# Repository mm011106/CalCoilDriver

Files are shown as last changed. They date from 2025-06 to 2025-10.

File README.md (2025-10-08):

<!-- 
基本資料はこちら：
BOXで、 ESM50902 を検索
SQUID用と比べて電流値が大きかも。
 -->

> [!NOTE]
> 資料などについてコメント等あればDiscussionsに投稿ください。

# 機器名
### **キャリブレーションコイルドライバ　ER-524D**

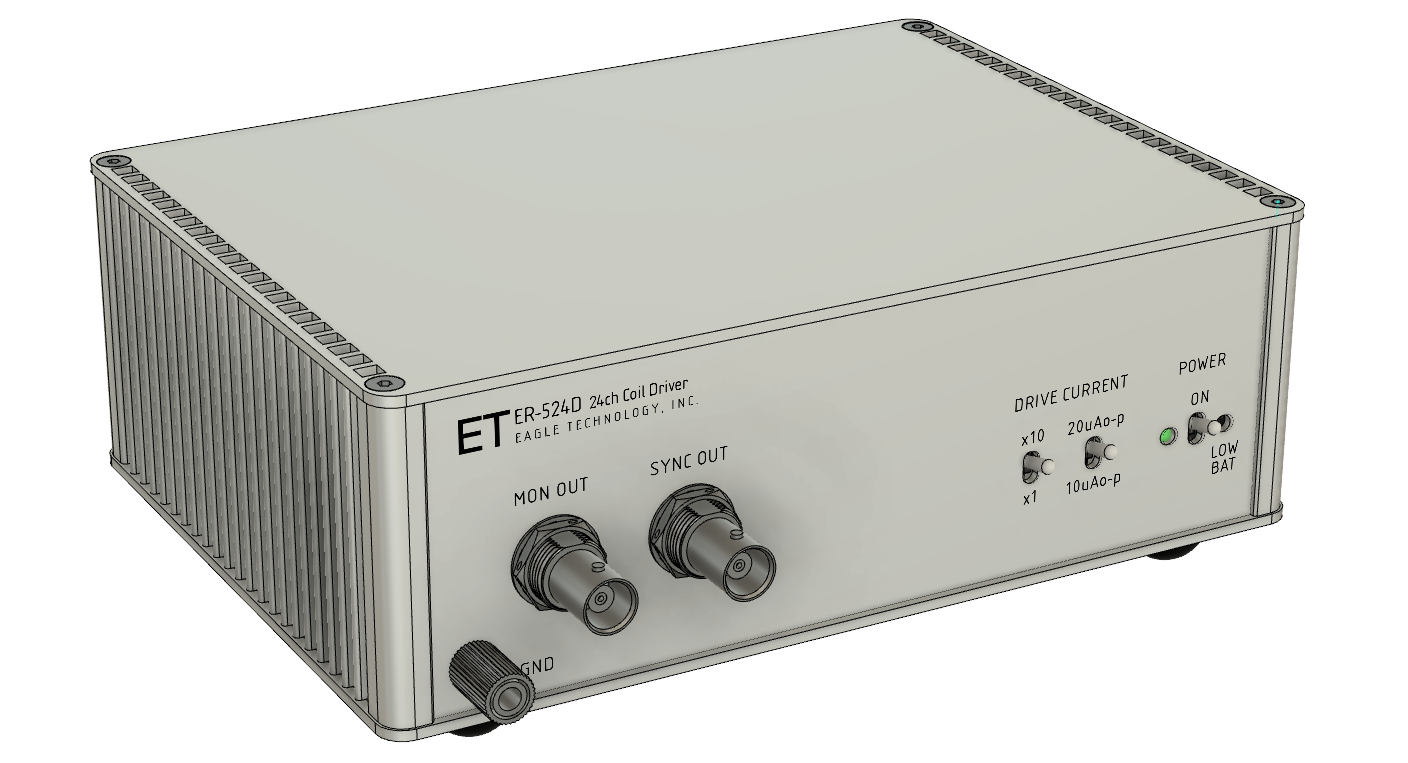
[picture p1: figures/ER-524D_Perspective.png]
3DPerspective


# 機器の概要

## 用途・目的
<!-- 本製品は磁気センサの感度・位置校正を行うための基準磁場を発生するためのコイルを定電流駆動する駆動回路です。
適切に設計・配置されたコイルでキャリブレーションコイルドライバにより基準となる磁場を発生させ、磁気センサから得られた磁場の強度信号とコイルドライバからの印加電流強度信号を以て磁気センサの感度・位置を校正することが可能です。 -->

複数の磁気センサをアレイ状に配置し磁場計測を行う場合、各センサ位置とその感度の両方を校正する必要があります。寸法や巻き数などのパラメタが管理されて製作されたコイル（キャリブレーションコイル）とそれを規定の電流で駆動する回路により基準となる磁場を発生させ、その磁場を計測することで校正が可能となります。この「キャリブレーションコイルドライバ」は校正作業に必要なキャリブレーションコイルを規定の電流で駆動するために設計された回路です。
> [!NOTE]
> 磁気センサの校正は以下の手順で行われます：
> 1. **センサとコイルの配置設定**：キャリブレーションコイル（複数）を校正対象の磁気センサに対して適切な位置に配置
> 2. **基準磁場の発生**：コイルドライバにより既知の強度の磁場を複数の異なる場所で発生させ、その磁場を校正対象のセンサで計測する
> 3. **信号計測**：発生した磁場の強度を磁気センサで測定すると同時に、コイルドライバのモニタ端子からコイルに流れた電流を計測
> 4. **校正実行**：両者の計測結果を基に磁気センサの感度と位置を校正

## 機能
- 交流の電流を各コイルに時分割で供給し駆動します。
- 各コイルの駆動はバースト波状の正弦波信号です。
- コイルを駆動する電流はパネルのスイッチで切り替えが可能です。
- コイルに流れる電流は電圧としてモニタができます。
- 流れている電流と上記のモニタ端子の電圧を測定器を用いて値づけすることにより、コイルに流れる電流値が計測できます。
- 単三型充電池4本で動作します。

## 性能
- 駆動信号周波数： 80Hz
- 駆動電流波形：正弦波
- 電流出力：200 / 100 / 20 / 10 [μAo-p]
- 駆動チャネル数：24（設計により変更可能）
 
> [!NOTE]
>  **駆動対象**
> 駆動の対象となるコイルは、十分直流インピーダンスが低く、インダクタンスが小さいことを想定しています。駆動回路の出力インピーダンスは10kΩ程度となっているため、コイルの直流インピーダンスが大きいと規定の電流を流せなくなる可能性があります（動作に支障はありません）。インダクタンスについては1mH以下を想定しています。駆動周波数80Hzでのコイルのインピーダンスが十分小さいことを条件として設計しています。
 <!-- 出力インピーダンス10kΩとして、1mH負荷のときのHPF遮断周波数は1.6MHz 一方、1mHの80Hzでのインピーダンス（リアクタンス）は0.5Ω -->

> [!NOTE]
>  **駆動回路**
> 駆動回路は高インピーダンス出力の非安定化電流源となっています。負荷接続時に定電流制御する回路は実装されていません。
> 負荷となるコイルがよく管理されて製造されているためコイルのインピーダンスのばらつきが非常に小さく、インピーダンスそのものも小さいと想定できたため、簡便な回路としました。

## バリエーション
本器の「負荷に電流を供給しその電流値を計測する」という機能により、生体磁場信号をエミュレートするための「ファントムコイル」をドライブすることに最適化した「ファントムドライバ」を作成可能です。磁場センサのキャリブレーションとは異なる電流設定（磁場強度設定）が必要な場合は出力電流の再設計が必要です。
> [!NOTE]
> **駆動電流の変更**
> 駆動電流の変更には回路定数の変更が必要となります。使用しているデバイスの性能から駆動電流の最大値は5mAo-p程度です。これ以上の電流が必要な場合は、回路定数の変更と同時にオペアンプの変更を検討してください。
>
> 

# 機器の構成 
コイルを駆動するための回路本体のみです。
キャリブレーションコイルそのものについては、この設計情報に含まれません。

# 動作の概要

### 駆動可能なコイルの数
この回路で駆動できるコイルの数は24個です。キャリブレーションコイルは３軸方向に磁場を発生させることを想定しており、３個のコイルが１つのコイルセットとなり、さらにそれを８個（３軸のコイルセットを８個）駆動できます。
駆動のための信号は多ピンコネクタ（ハーフピッチ50pin-SCSIコネクタ）に出力されますので、適宜コイルと接続するためのジグやケーブルの製作が必要となります。
> [!NOTE]
> 多ピンのコネクタは近年入手が困難になってきています。新たに製作される場合は3ピン〜6ピン程度の小型コネクタを複数利用するのが得策かと思います。

回路設計としては最大50個のコイルが駆動できるようになっていますので、ユーザの用途に応じてチャネル数を変更できます。

### 駆動波形
駆動は内部の正弦波発振回路に同期した正弦波のバースト波により時分割で行われます。駆動の様子を図示しました。
24個のコイルの駆動が1つのコイル駆動シーケンスとなり、それが繰り返されます。

まず、そのシーケンスの開始を示すため同期信号が正弦波の1周期の時間だけアサートされます。
同期信号がネゲートされると最初のコイルが駆動が始まります。
コイルは正弦波の24周期の時間だけ駆動され、1周期分の駆動休止時間が続き、次のコイルの駆動へと移ります。
最後のコイルが駆動された後、正弦波25周期分の長い駆動休止時間があり、コイルドライブの1周期が完了します。

駆動するコイルの順番やチャネル数、バースト波の波数と休止波数、正弦波の周波数は回路（HDL）で設定することができます。デフォルトでは、チャネル数24、正弦波の周波数80Hz、バースト波の波数24、休止波数1となっています。

<!-- 駆動用の正弦波は内部(DDSによる)で生成していますが、外部から供給することも可能です。この場合、信号の振幅が直接コイル駆動の電流値に変換されますので、供給する信号の振幅設定を確認してご利用ください。 -->

（下記「コイル駆動のタイミングチャート」を参照）

### 電流モニタ端子
コイルに流れる電流をモニタするための端子を備えています。
アナログ電圧出力で、0A = 1.65V となっています。
電流・電圧変換係数は、設計値で5033[V/I]となっています。

### 駆動電流の切り替え
駆動電流は、10μAo-p, 20μAo-p, 100μAo-p, 200μAo-pの４点切り替えです。
2つのトグルスイッチで設定します。

### 同期信号
24個のコイル駆動シーケンスの最初に正弦波の1周期の時間だけアサートされます。
レベルは0−3.3V、アクティブHi（正論理）です。

# 仕様
- ドライブコイル数：24
<br></br>
- 駆動電流 　(スイッチによる　4点切り替え)
  - 10/20/100/200μAo-p
<br></br>
- インターフェイス </br>
  - 同期信号出力：0−3.3Vロジック出力（正論理）
  - 駆動電流モニタ出力
    - アナログ電圧による（1.65V中心に+/-1V振幅）
    - 電流電圧変換係数：5033\[V/I] (設計値)
<br></br>
- 操作：フロントパネルトグルスイッチによる電源のOn/Off
<br></br>
- 表示
  - 電源電圧低下警告 Low-Battery（LED:赤）
  - 動作表示 (LED:緑)
<br></br>
- 電源：単三充電池（Ni-MH）4本
<br></br>

### コイル駆動のタイミングチャート
<!-- ![drive timing chart](figures/deriveSequence.png) -->
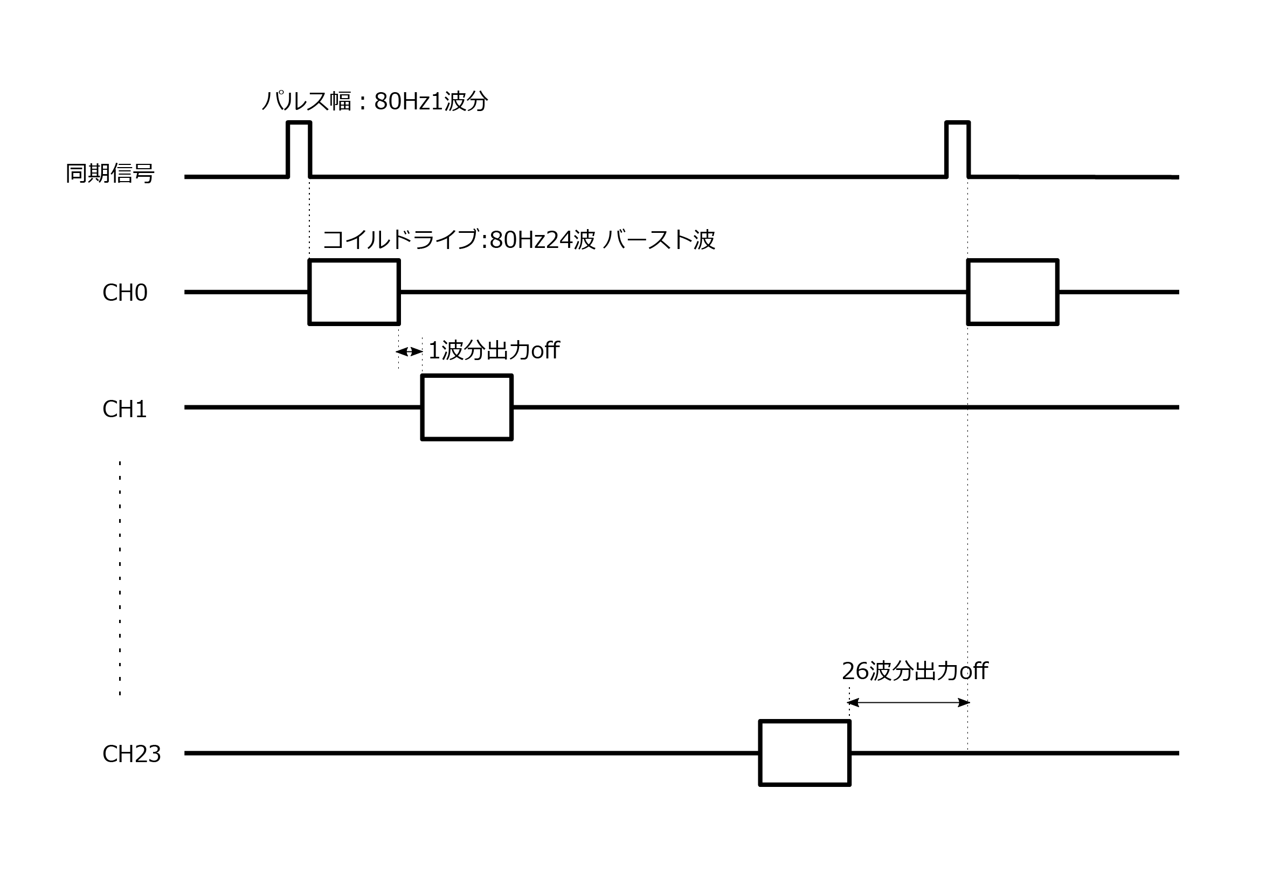
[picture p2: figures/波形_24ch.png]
drive_timing


### ブロック図
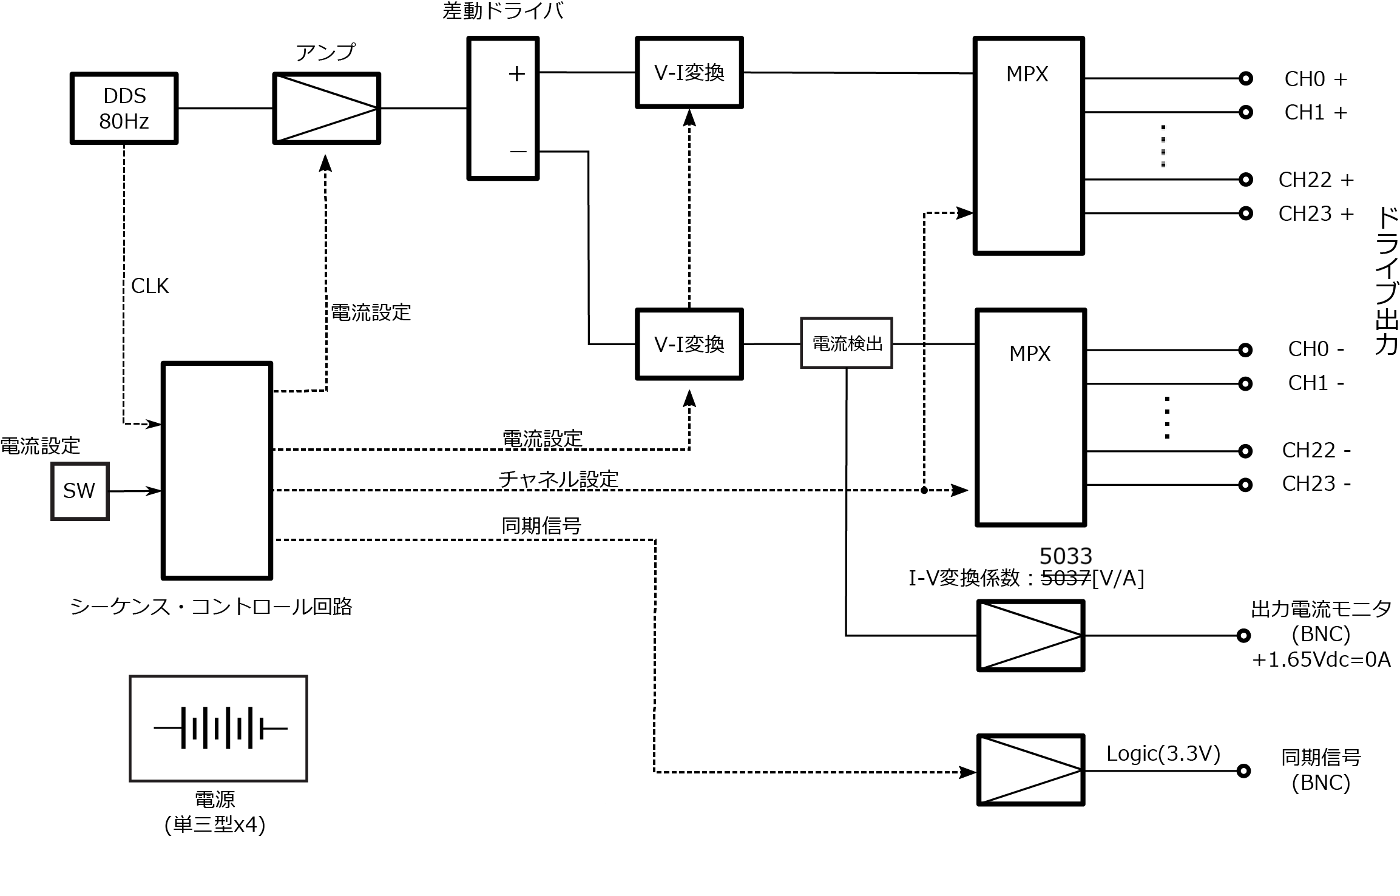
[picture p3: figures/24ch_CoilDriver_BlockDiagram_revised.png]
ER-524_BlockDiagram


</br>

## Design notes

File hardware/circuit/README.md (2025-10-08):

# このディレクトリについて

- このディレクトリにはPDF版の回路図が入っています。</br>
    CADを起動することなく回路図を確認することができます。

- 設計内容の詳細については[design_note](/hardware/circuit/design_note.md)を参照してください</br>

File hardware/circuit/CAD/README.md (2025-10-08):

# このディレクトリについて
このディレクトリは回路図・基板CADのプロジェクトが保管されています。</br>

CADにはEAGLEを使っています。 Ki-CADでインポート可能かと思います。

## 構成
[本体](/hardware/circuit/CAD/ER524D_CoilDriver24_EagleCAD/ER-524D_CoilDriver24.sch)：本体の回路図です。

[ハーネス](/hardware/circuit/CAD/ER524D_CoilDriver24_EagleCAD/harness_set.sch):装置内の盤間配線用ハーネスの回路図です。

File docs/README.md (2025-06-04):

# このディレクトリについて
このディレクトリは仕様書や製造に必要な書類、手順書などを保存してあります。

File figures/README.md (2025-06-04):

# このディレクトリについて
このディレクトリはリポジトリ内のドキュメントに挿入する図や写真などを保管する場所です。

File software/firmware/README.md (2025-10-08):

# このディレクトリについて

- このディレクトリはマイコンのファームウエア開発用IDEのプロジェクトフォルダを保管してあります。</br>
  この機器にはマイコンを使用しておりませんので、ファームウエアはありません。

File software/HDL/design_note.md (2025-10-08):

# 設計ノート
このノートは当該機器に使用しているHDLの設計意図を記録しています。</br>
回路動作の理解や改善・修理などにご利用ください

## 修正履歴
- 初版：2025/9/24  宮本政和

## 機能
- DDSを指定の周波数に初期設定する
- 80Hz発振器(DDS)をクロックとして、指定された波数と休止時間のバースト波を作るためのロジックと、それを最大50chのコイルに分配するためのチャネル指定信号を作成
- 機器の調整・試験のためのテストモードの設定

HDLのエンティティ名が`PHANTOMDRIVER`となっており製品型式名と異なりますが、回路設計の元となったコードのエンティティ名をそのまま残しています。
  
### ブロック図
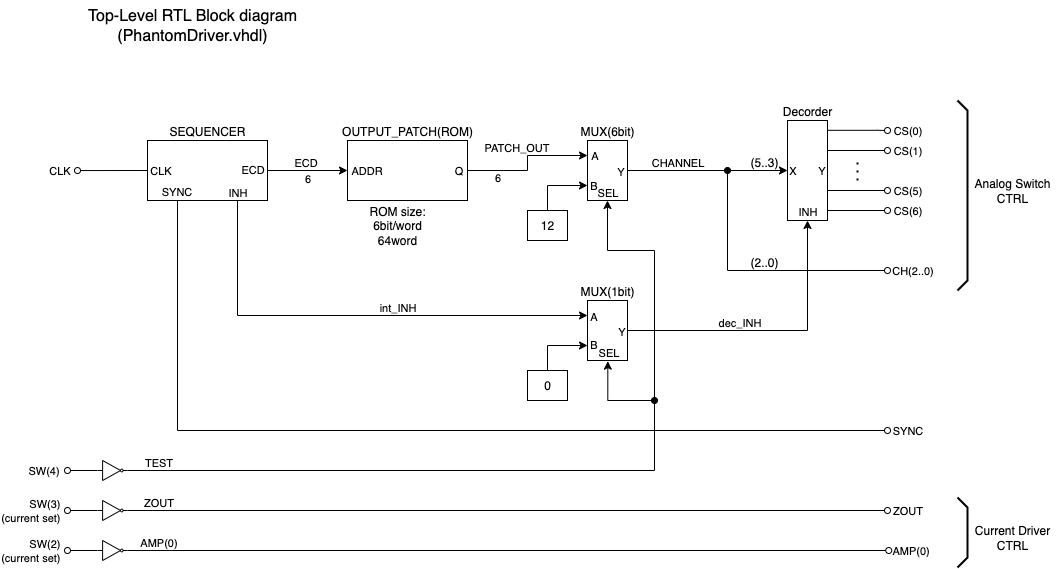
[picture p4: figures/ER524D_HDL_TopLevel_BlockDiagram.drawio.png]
Block Diagram for calibration

- DDSの初期設定回路については、このブロック図に記載していません

## 詳細動作
このHDLで記述されている機能は以下の通りです。
### 機能１ : DDSの初期化  ```DDS_INIT```
  DDSの出力が指定の周波数の正弦波になるよう初期化します。初期化にはSPIフォーマットのインターフェイスを用います。
  周波数はHDLのコンパイル時にハードコーディングされますので、周波数変更の場合はソースコードを変更しコンパイルが必要です。

### 機能2 : バースト波作成のための制御信号作成  ```SEQUENCER```
バースト波を作成するための制御信号をアナログ回路に提供し、連続した正弦波から指定された波数・休止のバースト波を作ります。
さらに規定の数のコイルを順次切り替えながらドライブするための制御信号を作成します。

### 機能3 : 駆動するコイルの切り替え  ```OUTPUT_PATCH``` ```MUX``` ```Decorder```
```SEQUENCER```からの信号を元にどのコイルをドライブするかを決定し、アナログ回路に提供します。

### 機能4 : ドライバ回路の設定  
フロントパネルにある電流設定スイッチの内容を読み、アナログ回路に提供します。

## 使用デバイス
- ALTERA MAX-V:  **5M160ZT100**
  - 温度グレード、スピードグレードは任意
- パッケージ：QFP-100pin

## ピンアサイン

| HDL信号名 | I/O |ピン番号 | 回路図信号名 |説明|
--|--|--|--|--
| CS[0] | O | 2 |#CS0|アナログスイッチCS信号
| CS[1] | O | 3 |#CS1|アナログスイッチCS信号
| CS[2] | O | 4 |#CS2|アナログスイッチCS信号
| CS[3] | O | 5 |#CS3|アナログスイッチCS信号
| CS[4] | O | 6 |#CS4|アナログスイッチCS信号
| CS[5] | O | 7 |#CS5|アナログスイッチCS信号
| CS[6] | O | 8 |#CS6|アナログスイッチCS信号
| LOW_BAT | I | 12 |#LOW_BAT|バッテリ低下検出
| CH[2] | O | 14 |CH_2|アナログスイッチチャネル設定信号
| CH[1] | O | 15 |CH_1|アナログスイッチチャネル設定信号
| CH[0] | O | 16 |CH_0|アナログスイッチチャネル設定信号
| OE    | O | 17 |#OE| （未使用）
| CLK   | I | 18 |SYNC_OSC| クロック入力（80Hz）
| AMP[0] | O | 19 |AMP_0| ドライブ回路電流設定（利得） 
| AMP[1] | O | 20 |AMP_1| ドライブ回路電流設定（利得）
| ZOUT   | O | 21 |ZOUT| ドライブ回路電流設定（インピーダンス）
| SEL_ANALOG | O | 26 | ANALOG / !DDS | 発振器指定出力
| SEL_EXT | O | 27 | EXT / #INT | 発振器外部・内部設定出力
| SW[5] | I | 51 |SW_DDS / #ANALOG|スイッチ入力 発振器指定
| SW[1] | I | 52 |SW_INT / #EXT|スイッチ入力 発振器外部・内部指定
| SW[2] | I | 53 |SW_x1 / #x2|スイッチ入力 ドライブ回路電流設定（利得） 
| SW[3] | I | 54 |SW_x1 / #x10|スイッチ入力 ドライブ回路電流設定（インピーダンス） 
| SW[4] | I | 55 |SW_#TEST|スイッチ入力 TEST動作設定 
| D[1] | O | 56 |DISP1|LED 発振器外部・内部表示
| D[2] | O | 57 |DISP2|（未使用）
| D[3] | O | 58 |DISP3|（未使用）
| D[4] | O | 61 |DISP4|（未使用）
| MCLK | I | 64 |MCLK| DDS:動作クロック
| SYNC | O | 66 |FRAME_SYNC|コイルドライブ同期信号
| PSEL | O | 70 |PSEL| DDS設定（未使用）
| FSEL | O | 71 |FSEL| DDS設定（未使用）
| RESET | O | 72 |RESET|DDS:リセット
| SDATA | O | 73 |SDATA|DDS:設定用SPI (DATA)
| SCLK | O | 74 |SCLK|DDS:設定用SPI (CLK)
| FSYNC | O | 75 |FSYNC|DDS:設定用SPI (STROBE)

---
## 回路構成
機能ブロックごとに詳細を記述します。

### ```DDS_INIT```
DDS-ICの初期化を行います。
- **INPUT:** </br>
    DDS_FREQ：DDSの周波数設定
    MCLK：DDSモジュールからのクロック(67.108864MHz)
- **OUTPUT:** </br>
    nRES, PSEL, FSEL, RESET：DDSのコントロール
    SDATA, SCLK, FSYNC：DDS設定端子(SPI)

#### 回路動作／設計のポイント
この回路は起動時に1回だけ動作する、DDSを初期化（周波数設定）する回路です。
設定はSDATA, SCLK, FSYNCの3つの端子(SPI)を操作することで行います。
この回路の動作クロックはDDSモジュールのクロック（67.108864MHz）から作成されています。
SPIのクロックは約1MHzに設定されています。

回路内に16bit長の設定データを3ワード分保持しており、これをMSBファーストでSDATA端子に出力していきます。
1ワードごとにFSYNC（負論理）の操作が必要で、この設計ではSPIクロックの1つ分の時間をFSYNCのアサート時間としています。

SPIにデータが出力される時のタイミングチャートを示します。参考にしてください。
<img src="/figures/HDL_DDS_INIT_SPI_timing.png" alt="Block Diagram for calibration" width="600px">

### ```SEQUENCER```
バースト波を作成するための制御信号をアナログ回路に提供し、連続した正弦波から指定された波数・休止のバースト波を作ります。
さらに規定の数のコイルを順次切り替えながらドライブするための制御信号を作成します。

- **INPUT:** </br>
  CLK: クロック入力（80Hz）
- **OUTPUT:** </br>
  SYNC: 同期信号
  指定数のコイルを順次ドライブしますが、その周期の最初に1回だけこの同期信号が１クロック時間だけアサートされます。
  INH: バースト波の「スペース」タイミングの指示
  この信号がアサートされている間、コイル駆動をoffにしてバースト波を作成します。
  ECD(6): コイルの番号
  この番号は'0'から'コイル数−1'の範囲となります。この数字は0からインクリメントされるので、この値を元に実際にどのコイルをドライブするのかを"OUTPUT_PATCH"で決定します。

この回路をインスタンス化する時のパラメータ指定例を示します。  
ここでは、コイル数24、バースト波 ON:24＋OFF:1
``` vhdl
-- コイル数の定義
  constant ECD_COUNT 	: integer :=24;   -- コイル数
  constant ECD_W		: integer :=integer(Ceil(log(real(ECD_COUNT-1),2.0)));   -- コイル数を数えるカウンタの幅

  constant BURST_MARK		: integer := 24;  -- バースト波の波数
  constant BURST_SPACE	: integer := 1;  -- バースト波の休止波数

-- インスタンス化
  SEQUENCER: entity work.SEQUENCER
    generic map (
      ECD_NUMBER => ECD_COUNT,
      ECD_Q_WIDTH => ECD_W, 
      BURST_MARK => BURST_MARK,
      BURST_SPACE => BURST_SPACE
    )
    
    port map (  -- 入出力信号の接続
      nRES => nRES, CLK => CLK,
      SYNC => SYNC, INH => int_INH, ECD => ECD
    );
```
  
#### 回路動作／設計のポイント
バースト波の波数をカウントするQ_BURSTカウンタと、コイルの番号をカウントするQ_ECDの2つのカウンタを設定しています。
これらの値から全コイルスキャンの同期信号SYNCと, アナログマルチプレクサを全てoffにして駆動のない状態を作るためのINH信号を作成しています。  
タイミングチャートを示します。参考にしてください。

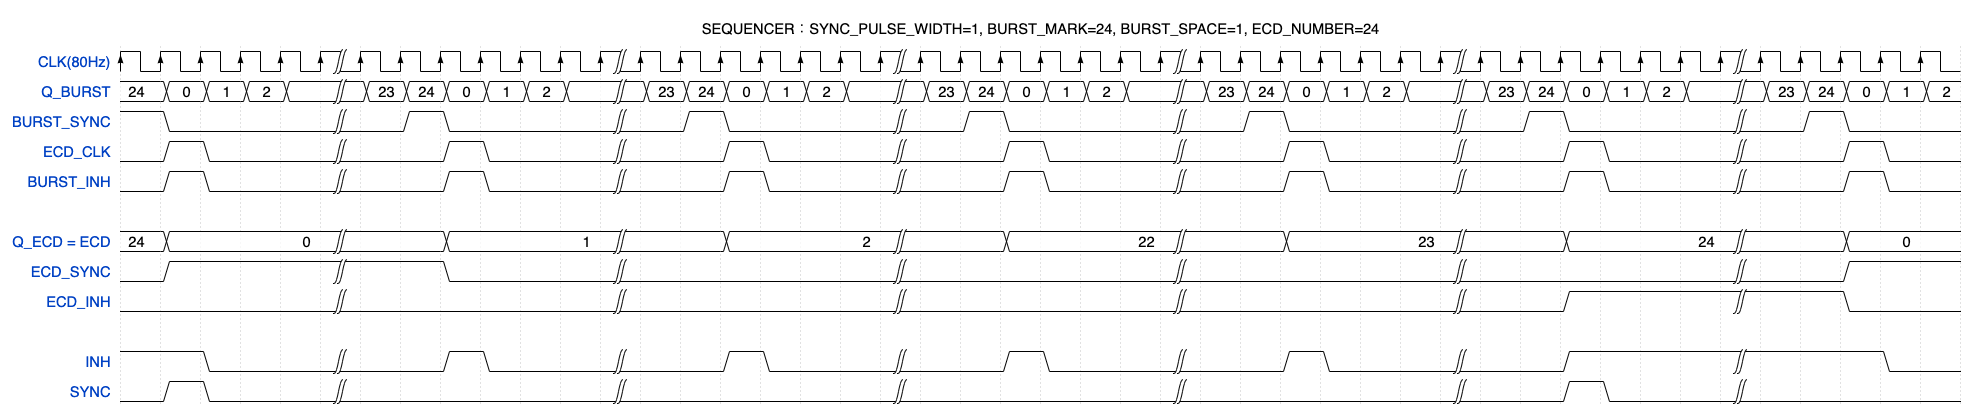
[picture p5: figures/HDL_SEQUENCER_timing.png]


### ```OUTPUT_PATCH```
```SEQUENCER```から出力されるECD番号をそれに対応するコイル番号に変更するためのROMです。

- **INPUT:** </br>
  ADDR: ECD番号の入力

- **OUTPUT:** </br>
  Q: ROMの値の出力
#### 回路動作／設計のポイント
これは単純なROMで、ADDRに入力された値からROMのデータを読み、その値をQに出力します。
この設計では、ADDRにSEQUENCERから出力されるECD番号が入力されその値に対応したコイル番号がQに出力されます。これにより、SEQUENCERでの番号（ECD番号）とコイル番号を対応づけています。
ADDR、Qともに6bit幅です。

ROMの値は ```patch_table.mif``` というファイルにテキスト形式で記述されています。

### TESTモード設定
コイルドライブの電流値キャリブレーション作業用にドライブするコイルを固定する回路です。
コイル番号を固定し、出力インヒビット信号を常にネゲートすることで、駆動するコイルを固定します。
（ブロック図中央、二つの```MUX```）

### ```Decorder```
- **INPUT:** </br>
  CHANNEL(5..0) : コイル番号
- **OUTPUT:** </br>
  CS(0)〜CS(6) : アナログマルチプレクサドライブ用チップセレクト信号
  CH(2..0) : アナログマルチプレクサドライブ用チャネル設定信号
  
#### 回路動作／設計のポイント
この回路の出力が直接アナログマルチプレクサIC14個（ドライブのプラス側、マイナス側それぞれに1個づつ使用）を制御します。
この信号によって制御されたアナログマルチプレクサにより、規定のバースト波が作られると共にコイルのスキャンが行われます。

## 注意事項
コイル数、バースト波などの設定をパラメタ化して任意の組み合わせで合成できるようにしていますが、全ての設定値の組み合わせでコンパイルが成功することを確認していません。パラメタを変更した場合は動作を確認してからご利用になるのがいいと思います。  

<!-- ## 変更履歴
##### 20xx/xx/xx Release1.0
- リリース内容メモ -->

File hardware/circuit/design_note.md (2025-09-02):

# 設計ノート
このノートは当該機器の電子回路設計の履歴や設計意図を記録しています。</br>
回路動作の理解や改善・修理などにご利用ください

## 修正履歴
- 初版：2025/06/01  宮本政和

# 設計の概要
## ブロック図
ER-524_BlockDiagram

## 設計のポイント
- **バッテリ動作**  
  単三バッテリ4本で動作するように設計しました。  
  ACでの駆動は磁気計測環境に対してノイズを導入する可能性があるため、信頼性の高い計測が必要なキャリブレーションには向かないと判断しました。
  コイルドライブ部の駆動電圧は3.3Vですが、出力をプッシュプル構成とすることで動作電圧が低いという欠点を補っています。

- **DDSを発振器として利用**  
  <!-- 従来のコイルドライバではアナログの発振器を使用していましたが、この設計ではDDSに変更しました。  
  これにより周波数変更作業が容易になります。従来、周波数変更のためには発振回路の抵抗器の交換が必要でしたが、この設計ではCPLDに書き込むHDLの変更（ソフトでの対応）で済む様になりました。
  一方、DDSは高周波で動くデジタル回路ですので、コイルドライブ回路へのノイズの流入に注意して設計しました。  
  アナログの発振回路も回路図上は残っていますので、必要に応じて利用可能です。 -->

  従来のコイルドライバではアナログ発振回路を用いていましたが、本設計ではDDSを採用しました。これにより、周波数変更の作業がソフトウェアで完結するため、ハードウエアの改修（抵抗交換）不要となり、周波数の変更にも容易に対応できます。
  一方で、DDSは高速なデジタル回路であるため、アナログ回路であるコイル駆動回路へのノイズ影響を最小限に抑えるよう配慮して設計しました。  
  アナログ発振回路も残しているため、用途に応じて使い分けることが可能です。

- **コイル駆動電流を計測できる様にモニタ端子を用意**   
  キャリブレーション作業では、コイルに流れる電流を計測する必要があります。そのための電流モニタ回路を用意しました。
  コイルに流れる電流値をアナログ電圧として計測することが可能です。さらに、実際にコイルに流れている電流を別法により計測することで、電流モニタ回路出力の値を校正（値付け：あたいづけ）することができます。
  電流モニタ回路は安定した計測結果を得るために、温度特性に優れた部品を使っています。
  
# 各部の詳細設計
この設計では機能を、市販の「DDS回路」と設計した「本体回路」で実現しています。  
以下の順を追って各回路の設計について解説します。

## 発振回路(DDS)

### 設計のポイント
コイルを駆動する信号を生成するためのDDS回路です。  
<!-- 
発振回路そのものは市販のモジュールを利用しています。DDSでは周波数決定のためのレジスタに設定する値と、デバイスに接続している水晶発振子の発振周波数から出力される信号の周波数が決定されます。そのため例えば、周波数設定値のLSB1ビット分を0.1Hzにする、と言ったような「キリのいい」設定にしようとすると、水晶発振子の周波数が2^24/10のような値になってしまい、標準的でない「特注周波数」での購入になってしまいます。そうするとコストも納期もかかってしまうので、市販のモジュールを使用することにしました。  
使用したモジュールは ストロベリーLinuxという会社の「AD9834 小型DDSモジュールキット」という製品で、AnalogDevicesのAD9384というDDS-ICと特注の水晶発振子を実装しており、周波数設定の1LSBあたり0.25Hzとキリのいい周波数設定で出力信号の周波数を設定できるようになっています。  
また、出力信号が差動で得られるのでノイズ対策にも有利です。 -->
DDSは、周波数決定レジスタに設定する値と基準クロック周波数（水晶発振子）によって出力周波数が決まります。しかし、周波数設定の分解能（1LSB）をキリの良い値（例えば0.1Hz）にしようとすると、基準クロック周波数が非標準的な値になってしまい、特注の水晶発振子が必要となります。これはコスト増や納期遅延の原因となるため、水晶発振子が実装済みの市販モジュールを利用することにしました。  
採用したのは、ストロベリー・リナックス社の「AD9834 小型DDSモジュールキット」です。このモジュールは、Analog Devices社のDDS-IC「AD9834」と特注の水晶発振子を搭載することで、周波数分解能を0.25Hz/LSBという扱いやすい値に設定しています。  
また、差動出力に対応しているため、ノイズ対策の面でも有利です。
<p>
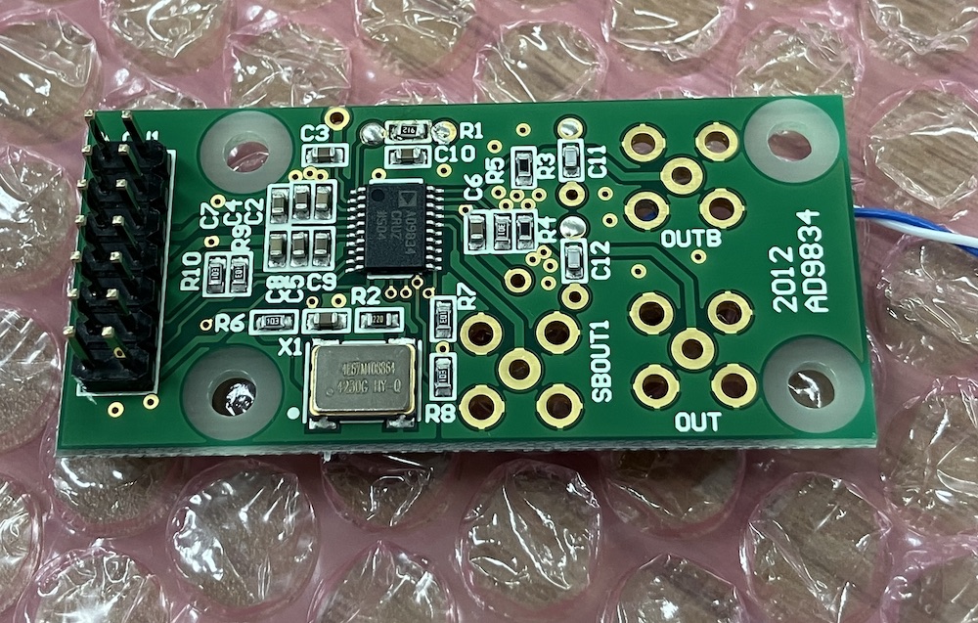
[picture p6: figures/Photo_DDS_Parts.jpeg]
DDS_photo1

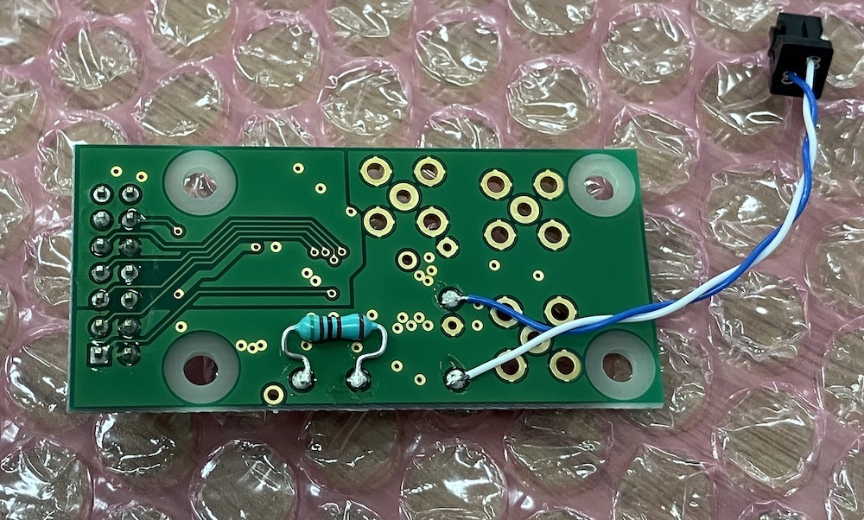
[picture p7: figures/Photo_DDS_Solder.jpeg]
DDS_photo2

</p>

### デバイス仕様・定数の決定
回路図にはこのDDSモジュールの設定について記載していないので、ここに記載しておきます。
- メーカ、品名：[ストロベリーLinux　AD9834 小型DDSモジュールキット](https://strawberry-linux.com/catalog/items?code=57090)
- 周波数設定：CPLDのプログラミングによる（デフォルト：80Hz）
- 出力信号：差動出力　0.25Vo-p
  - これを本体側の差動アンプ（ゲインx1）回路で受けるので、本体側の信号レベルとしては2倍の1Vp-p(=0.5Vo-p)になります。
  - 出力設定のために、本体上の出力電圧設定抵抗（FSADJ端子につながっている6.8kΩの抵抗）を取り外し、8.66kΩ(=9.1kΩ//180kΩ)を取り付けます。
  - 信号はDDSモジュール上のSMBコネクタのパターン上からリード線を引き出しDF11コネクタを取付け、本体回路のCN1と接続しています。
- 電源電圧：3.3V
  - モジュールの仕様としては電源電圧5Vです。初期の設計でDDSを5V動作に設定して動作確認したところ、CPLDのIO電圧が3.3VであるためDDSがCPLDからのコマンドを受け取れないという状況になりました。そのため、3.3V動作としています。
  - 使用しているDDSデバイスの電源範囲は2.3〜5.5Vなので問題ないですが、使用している水晶発振器の電源電圧が5Vとなっています。実際に動作テストを行い、3.3Vでも問題ないことを確認してこの電源電圧で使用しています。

### 組み立て
- 本体回路と接続するため付属のコネクタ（ピンフレーム：ピンヘッダが嵌合するメスのコネクタ）をはんだ付けします。部品面にコネクタを実装し、ハンダ面からはんだ付けします。
- SMAコネクタが付属していますが使用（実装）しません。
- 出力電圧設定のため、実装されているR1を取り外し180kΩを取り付けます。さらにリード抵抗で9.1kΩをR1にパラに接続します。
- IOUTとIOUTB端子にケーブルをはんだ付けし、ツイストさせてDF11コネクタ4ピンメスを接続します。

## 本体回路
本体の回路は以下のような機能が実装されています。

- アナログ発振回路（未使用）
- 外部入力回路（未使用）
- DDS信号入力回路
- 入力選択回路（固定で使用）
- シーケンス駆動用クロック信号生成回路（コンパレータ）
- ドライブ回路／電流設定回路
- 電流検出回路
- 中間電位生成回路
- バッテリ電圧監視回路
- 電源回路
- マルチプレクサ回路
- ユーザインターフェイス回路
- 同期信号出力回路
- DDSインターフェイス
- シーケンス回路（CPLD/HDL）

以下に、各部の設計の詳細について記載します。

## 回路図 1/4
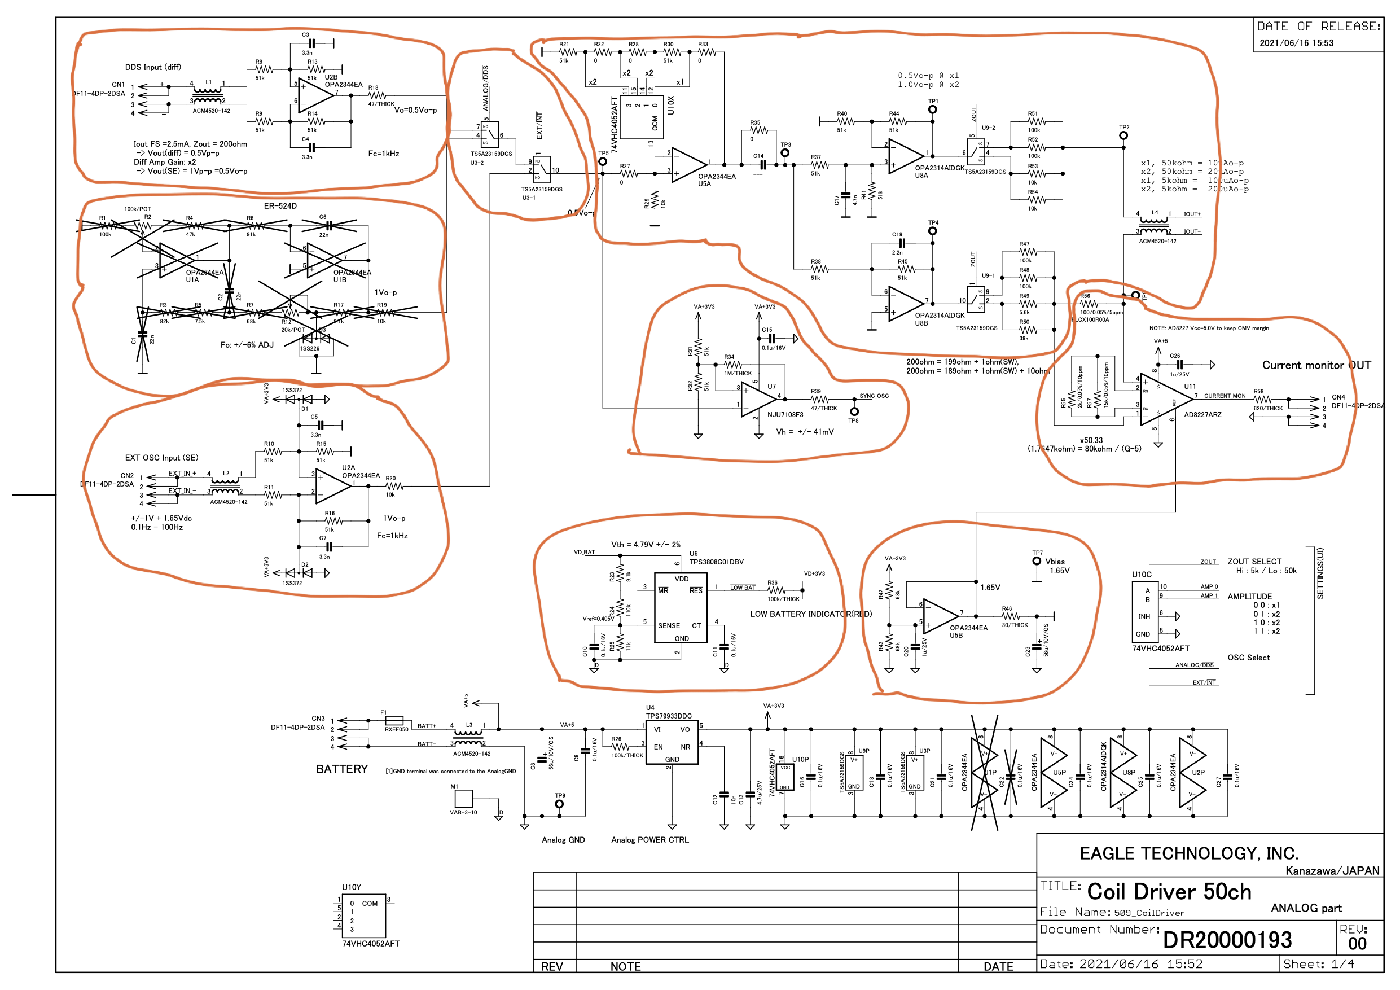
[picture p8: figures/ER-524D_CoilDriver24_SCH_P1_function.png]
CKT_page1


### アナログ発振回路（未使用） (U1A,U1B)
コイルを駆動する信号を生成するアナログの発振回路です。今回の設計では使いませんが、旧バージョンとのコンパチビリティのために基板上にパターンが存在します。  
部品を実装すれば利用可能です。発振可能な周波数範囲としては10Hzぐらいから20kHz程度かと思います。ドライブ回路ではノイズ対策のためLPFが入っていますので、周波数を変更する場合はその調整も行ってください。  
出力電圧は1Vo-pに調整します。振幅電圧が低いと安定して発振できなくなります。

### 外部入力回路（未使用） (U2A)
コイルを駆動する信号を外部から入力するための回路です。今回の設計では使用していません。  
差動アンプで受けることで外部の発振器からのノイズ流入を抑えています。  
0.5Vo-p入力時に設計した駆動電流となります。

### DDS信号入力回路 (U2B)
DDSのアナログ出力を受け取ります。DDSからのノイズ流入を防ぐため、GNDを直接接続しない差動アンプで受け取ります。差動アンプの利得は1倍ですが、DDSの出力も差動なのでDDSの設定電圧の2倍の電圧が出力されます。
DDSのDAコンバータによる高調波ノイズを抑えるため、1kHz程度のLPFがかかっています。

### 入力選択回路（固定で使用） (U3-1,U3-2)
アナログスイッチを用いて、コイルを駆動する信号をCPLDの信号により選択します。DDS、アナログ発振回路、外部入力の3つの選択肢があります。  
今回の設計では、CPLD内部でDDSに固定されています。

### シーケンス駆動用クロック信号生成回路（コンパレータ） (U7)
複数のコイルを決まったパターンで順次ドライブするための、チャネルの切り替え信号などを生成するためのシーケンス回路が必要となります。そのシーケンス回路の動作タイミングの基準となるクロックを発振回路の出力信号から作成するのがこの回路です。  
単純なヒステリシス付きコンパレータで、発振回路の出力の正弦波から矩形波を作成し、CPLD内のシーケンス回路に渡します。  
ヒステリシスは41mVに設定してあります。このヒステリシスで現在のところ問題は発生していません。

### ドライブ回路／電流設定回路 (U5A,U10X,U8A,U8B)
入力選択回路からの正弦波はドライブ回路に入ります。入力電圧は0.5Vo-pです。  
アナログ発振回路からの信号は1Vo-pなので、入力で1/2にアッテネートされます。DDS入力の場合はそのまま入力されます。  
最初にU5AとU10Xの非反転アンプで出力電流設定に応じて、1倍もしくは2倍に振幅を増幅します。

その後、プッシュプル動作のドライブ回路(U8A,U8B)に信号が渡されます。ここでは1倍の反転アンプと1倍の非反転アンプの構成でプッシュプル（差動）出力の信号を作成します。ノイズ防止のため1.4kHz程度のLPFがかかっています。  
プッシュプル出力の信号はそれぞれU9のアナログスイッチを通して出力電流を決める抵抗に接続されます。ここでは２つの出力インピーダンスを切り替えて電流出力を設定しています。この設計では2つのインピーダンスの比は10倍です。  

電流の切り替えは、最初の非反転アンプU5Aでの電圧での切り替えと、この出力インピーダンスの切り替えの2箇所で行うことになります。それぞれ1bitの切り替え選択肢なので、4つの設定ができることになります。

この設計では定電流駆動回路の構成は取りませんでした。接続されるコイルが既知の仕様のものであり、インピーダンスが十分低いことがその理由です。定電流駆動回路は、負荷のインピーダンスが未知だったり、ばらつきが大きいものを安定して定電流で駆動することができます。その一方で回路が複雑になり信号に対する応答特性を考慮する必要があること、3.3Vという低電圧動作のため定電流駆動回路の利点が引き出せない可能性があることから、単純な高出力インピーダンスによる電流出力としました。

出力インピーダンスを下げることによってドライブ電流を上げることができますが、オペアンプのドライブ能力の点から5mA程度が最大となります。また、インピーダンスを下げるとコイル接続部の接触抵抗などによるドライブ電流誤差が大きくなると考えられます。  
ドライブ電流は計測できるので大きな問題にはならないと思いますが、計測の安定性や信頼性を考えるとコイルのインピーダンスの100倍程度の出力インピーダンスは維持した方がいいと思われます。

### 電流検出回路(U11)
コイルの駆動電流を検出する回路です。高精度の抵抗(100Ω)をコイル駆動出力に挿入し、高利得確度のインスツルメンテーションアンプICを利用してその両端の電圧を測ることで電流を測定することを可能にします。  
インスツルメンテーションアンプの利得は高安定度の抵抗2本の並列接続(R55,R57)で設定しています。これにより利得は50.33倍に設定されます。100Ωの電流検出抵抗を使っているので、電流電圧変換係数としては5033[V/I]となります。   
例えば10uAで駆動した場合、電流検出回路出力は50.33mVになります。

<!-- 電流電圧変換係数の誤差は、インスツルメンテーションアンプの利得誤差（0.3%最大）、利得設定抵抗の抵抗値誤差（0.05%最大）、電流検出抵抗100Ωの誤差(0.05%最大)から見積もれますが、これは理想的な状況を仮定した場合だと考えられます。実際には部品実装時の熱ストレスやハンダ付けによる機械的なストレスが加わっており、部品単体の仕様で提示された誤差よりも 大きくなる可能性があります。
完成後にコイル駆動電流値と電流検出回路の出力の電流の両方を同時に計測することにより電流電圧変換係数の値付をする必要があると考えます。
-->

インスツルメンテーションアンプのコモンモード電圧について検討してみます。
この回路の後段には24個のコイルを順次駆動するためのマルチプレクサが控えています。シーケンス回路によってコイルが切り替わる時にマルチプレクサがオフになり電流駆動回路がオープンになる時間があります。コイルがつながっていて電流駆動している場合、インスツルメンテーションアンプのコモンモード電圧は、電源電圧(3.3V)の中間電圧である1.65V程度になりますが、電流駆動が開放の場合はドライブ回路のオペアンプを通じて1.68V±1Vの電圧がかかることになります。  
データシートを見てみると、コモンモード電圧の最大は電源電圧−0.9Vとなっており、3.3Vの電源電圧だと2.4Vとなり、1.68V±1Vの入力があった場合には一部オーバーロードとなり出力信号が異常となってしまいます。そのためインスツルメンテーションアンプの電源のみ、3.3Vではなくバッテリから直接供給することとしました。   
バッテリはNi-MHを4本使用する設計としましたので、標準的には1.2x4=4.8V程度の電圧が期待でき、バッテリが減ってきた状態でセルあたりの電圧が1.1V程度に落ちたとしても、電源電圧4.4V程度ですのでコモンモード電圧の最大は3.5Vとなり、マルチプレクサがオフのコイルを電流駆動していない場合でも安定した出力を得られることになります。

この回路の出力はBNCコネクタを経由して外部の機器に接続されます。ケーブルの長さが長い場合(5mを超えるような場合)にインスツルメンテーションアンプの出力が発振するという現象があったので、出力インピーダンスを高く設定しています。接続する機器の入力インピーダンスに注意してください。

### 中間電位生成回路（U5ｂ）
オペアンプで構成した反転・非反転増幅回路の基準電圧を作るための回路です。  
電源電圧を抵抗分割で半分にして回路の基準電圧(1.65V)としています。この電位は電流検出回路の出力の中間電位設定用にも供給されていますが、駆動回路の動作時の電流流れ込みによる基準電位の変動を抑えるため、CRで分離しています。  

### バッテリ電圧監視回路(U6)
<!-- バッテリが消費されて電源電圧が低下したことを知らせるため、バッテリ電圧監視回路が実装されています。  
電圧監視の専用IC(U8:TPS3808G01)を利用し、アラーム発呼のスレッショルドを4.79Vとしました。
電池はNi-MH 単三型4本 の利用を前提としており、1本あたり1.2Vが規定の出力電圧です。スレッショルド電圧の4.79Vは電池1本当たりにすると1.1975Vとなり、1.2Vを切るぐらいのところでワーニングが出るようになります。"eneloop(容量:1.2V 2Ah)"を使った放電実験のwebサイトなどを参照すると、0.2Cの放電率で使用した場合、1.2Vを切ると急激に出力電圧が低下する様子が見て取れましたので、1本あたり1.2Vでワーニングが出るようにしました。  
実際の消費電流は10mA~20mA程度ですので2Ahのバッテリに対して放電率0.01C程度となり、バッテリ1個あたりの電圧1.2Vを切って使用し続けてもしばらくは動作するように思えます。 -->

本機器には、バッテリー電圧低下を知らせるための監視回路を実装しています。
監視ICには、TPS3808G01 (U8) を採用し、アラーム発生のスレッショルド電圧を 4.79V に設定しました。この値は、単三形Ni-MH電池4本を想定しており、電池1本あたりの電圧に換算すると 1.1975V となります。  
アラーム発生のスレッショルド電圧を決めるにあたり、Webサイトの放電実験データ（例：eneloop 1.2V 2Ah、放電率0.2C）を参照しました。その例では、放電率0.2Cでの使用時に、電池電圧が1.2Vを下回ると急激に電圧が降下する傾向が見られたため、電池1本あたりの電圧1.2Vを警告の目安としました。  
実動作時の消費電流は10mA～20mA（放電率0.01C程度）と小さいため、警告後も直ちに動作停止することはありません。フロントパネルの赤色LED点灯により、バッテリー交換/充電時期をお知らせします。  
ローバッテリのワーニングが出ても、LEDが点灯するだけで動作に支障はありません。

### 電源回路(U4)
バッテリの電圧は使用時間に応じて変化するので、安定した電圧を供給するために3.3Vのレギュレータを使っています。  
ドロップアウト電圧は0.1Vのデバイスを使っていますので、理論的にはバッテリ電圧が3.4Vまで低下しても正常に動作しますが、この電圧はバッテリにとって過放電の状態ですので、ローバッテリのワーニングが出たらバッテリを充電してください。 
バッテリからの電源入力の直近にはポリヒューズを挿入して基板上での電源ショート時に電池を遮断するようにしています。

## 回路図 2/4
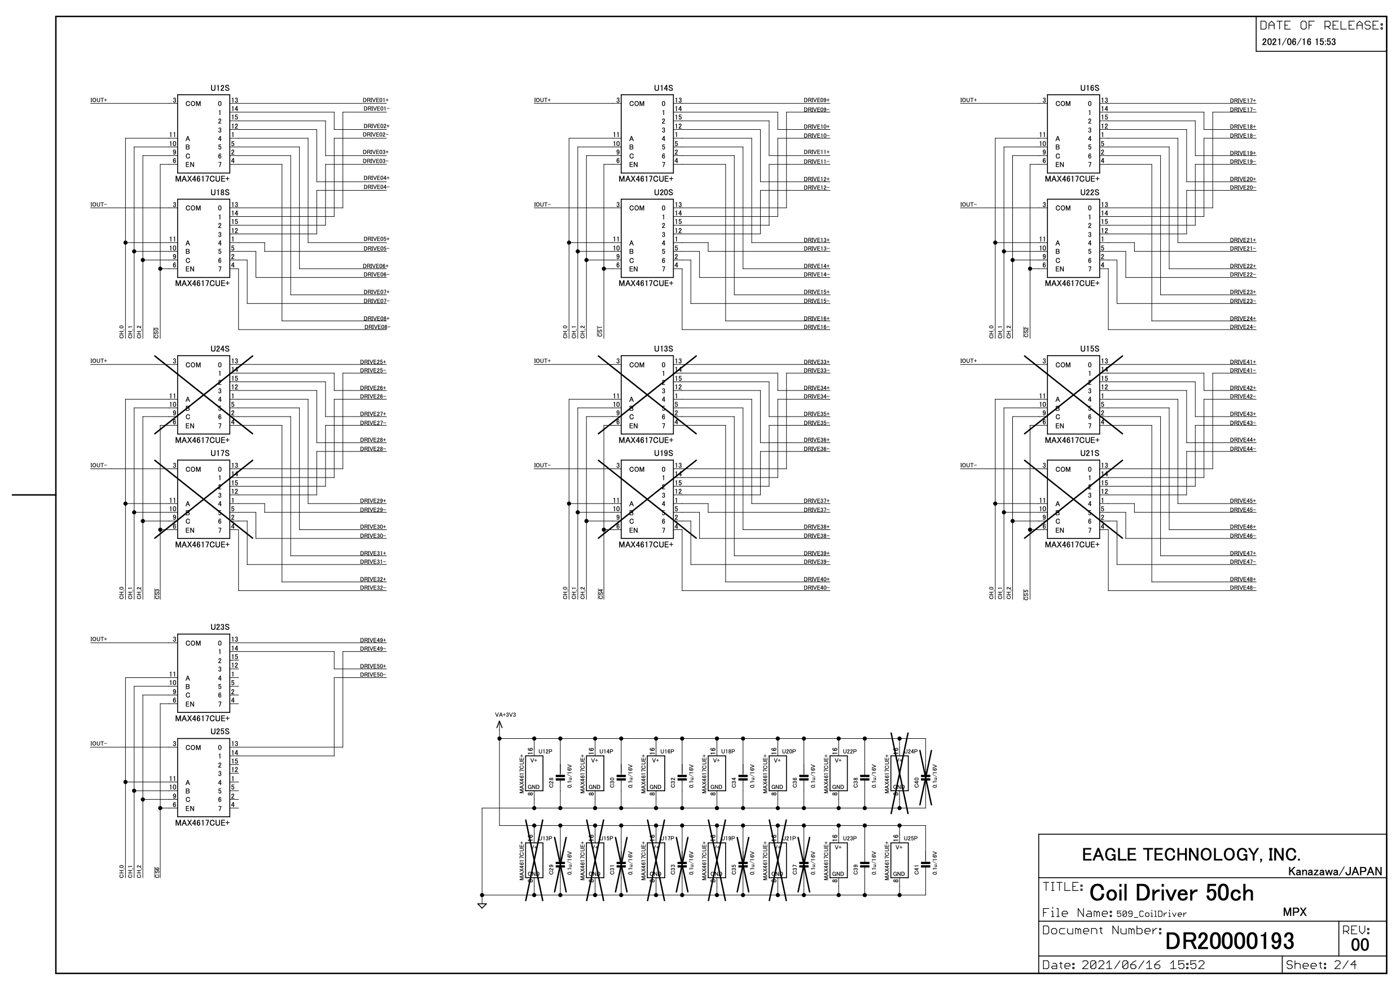
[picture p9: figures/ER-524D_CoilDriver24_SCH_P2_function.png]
CKT_page2


### マルチプレクサ回路
24個のコイルを順次切り替えて駆動するためのマルチプレクサ回路です。この回路図では最大50個のコイルまで駆動できるようにマルチプレクサ回路を組んであります。  
8ch切り替えのアナログスイッチ7個をプラス側とマイナス側で1セットづつ、合計14個使います。それぞれのアナログスイッチにはチャネルを設定する3bitの信号と、チップセレクトがあり、これらを組み合わせて50chの切り替えを実行します。スイッチにはリーク電流が少ないタイプのものを選んでいます。スイッチのリーク電流は内部の寄生ダイオードによる電源からのリークなので直流であることが想定される一方、今回の設計では交流駆動であるため直流リーク電流による測定への影響は小さいと考えています。ただ、スイッチのリーク直流がコイルに流れ、磁場が発生している可能性は否定できません。

## 回路図 3/4

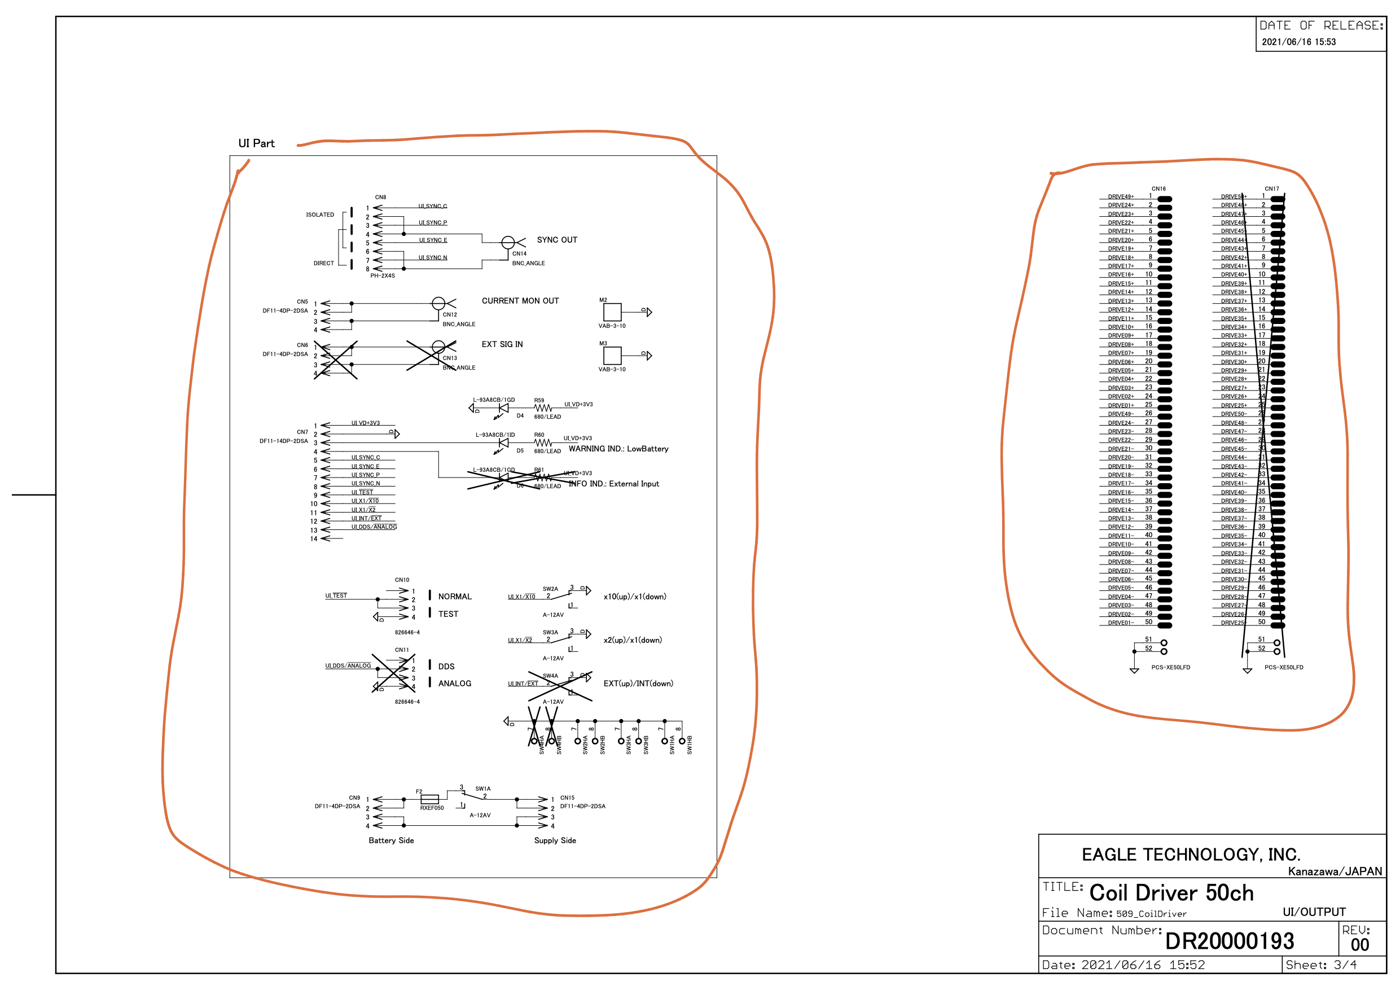
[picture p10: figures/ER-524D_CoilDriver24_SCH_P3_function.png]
CKT_page3


### ユーザインターフェイス回路
フロントパネルに出ている、スイッチ、BNCコネクタ、LEDなどユーザへのインターフェイスを提供する部分を集めた部分で、本体とは別の基板に実装されます。メイン基板とはCN7のコネクタで接続します。また、電池からの電源はいったんこの基板上で電源スイッチを経由したのち本体に渡ります。  
同期信号の出力を選択する回路は、BNCコネクタに出力する信号を「フォトカプラでアイソレートされた信号」もしくは「直接ドライブされる信号」にするのかを選択します。これは基板上のジャンパで行うものでフロントパネルから操作はできません。  
その他、電流設定スイッチ、パイロットランプ(LED)、ローバッテリワーニング(LED)が実装されます。

### コイルドライブ出力コネクタ
マルチプレクサからの電流出力を外部に出力するためのコネクタです。50ピンSCSIコネクタ2個で50ch分の信号を外部に出力しています。この設計では24chのドライブですので、その半分だけ、1個のコネクタを使います。  
コネクタの出力ピンは25列上下２段構成になっているので、その上下で1セットのコイルを接続すように設計してあります。  
マルチプレクサのチャネル指定とこの出力コネクタのピン番号の関係は以下のようになっています。ピン番号とチャネル指定番号とは昇順・降順が逆になっているので注意してください。

|MUX channel   |Signal name  |Connector Pin Num|
|---|---|---|
|0  |DRIVE01         |25/50 |
|1  |DRIVE02         |24/49 |
|2  |DRIVE03         |23/48 |
|:  |:         |: |
|21  |DRIVE22         |4/29 |
|22  |DRIVE23         |3/28 |
|23  |DRIVE24         |2/27 |

## 回路図 4/4

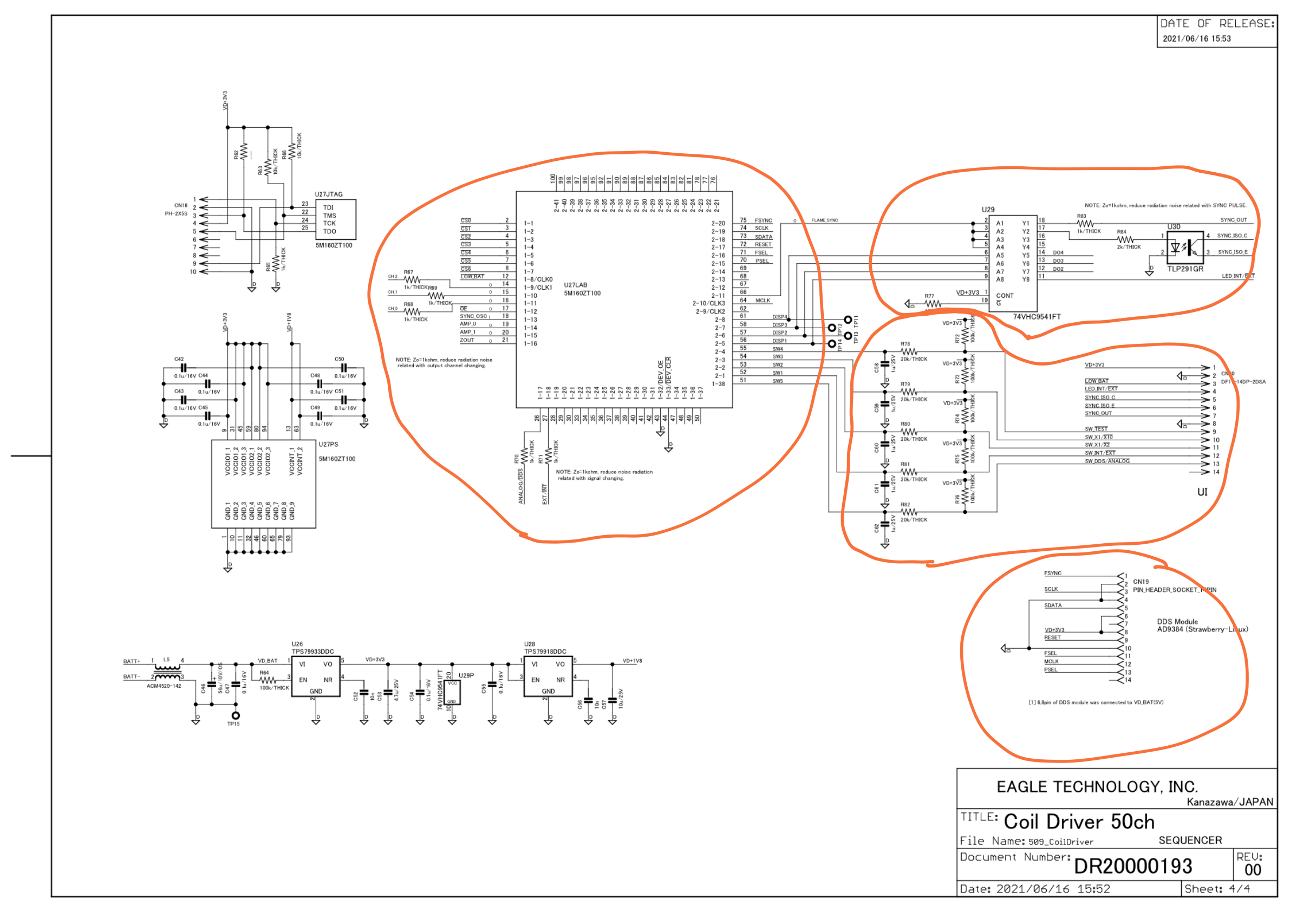
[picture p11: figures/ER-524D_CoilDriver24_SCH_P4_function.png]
CKT_page4


### 同期信号出力回路
同期信号を出力する回路です。ラインドライブ用のIC(U29)を用いてドライブ能力を強化しています。また、絶縁信号の出力を用意するためにフォトカプラを使っています。フォトカプラは同期信号を受け取る装置と本装置の間でGNDループを形成しないようにする目的で導入されています。高耐圧の絶縁用途として設計されていません。  
フォトカプラによる絶縁出力は、信号の受け側に電源が必要になりますので注意してください。

### スイッチ接続回路
ユーザインターフェイス回路からのスイッチ入力および、表示用LEDのドライブを行う回路です。  
スイッチ入力にはチャタリング除去用のCR回路があります。LEDドライブのためにバッファIC(U29)を利用しています。

### DDSインターフェイス
DDSの設定のためのシリアルインターフェイス(SPI)がCPLDに実装されており、そこからの信号をDDSに接続しています。 
DDSのクロックをCPLDに渡して、そのクロックからDDSとCPLDの通信に使用するSPI信号を作成しています。SPIの他、DDSを制御するための信号線もCPLDに接続していますが、この設計では積極的に利用していません。

### シーケンス回路（CPLD/HDL）
80Hzのクロック信号を元にマルチプレクサ回路を駆動するシーケンス回路をCPLDに実装しています。  
詳細についてはHDL設計図書をご覧ください。マルチプレクサ回路の駆動の他に、ユーザインタフェース回路からのスイッチの設定情報から出力電流を設定したり、電源投入時にDDSのイニシャライズをしたりといった機能を実装しています。  
CPLDの電源はアナログ回路へのノイズ流入を防ぐため、アナログ回路とは独立したレギュレータでデジタル部分の電源を作成しています(U26,28)。I/O電圧が3.3V、コア電圧が1.8Vとなっており2つのレギュレータが必要になります。  
物理サイズは100ピンのQFPパッケージで、回路規模は160LEです。部品実装作業の簡便さからQFPパッケージを選んでいますが、実装面積が大きくなってしまいました。小型のBGAなどのパッケージもありますのでお好みでご利用ください。  
プログラミング用のJTAG端子(CN18)はALTERA USB blasterとコンパチビリティがあります。

## ハーネス
筺体内の配線のためのハーネスの詳細については、[ワイヤハーネスの回路図](harness_set.pdf)を参照ください。  
ケーブルは手元に在庫があった潤フロン線(AWG30)をつかっていますが、AWG26〜28程度の細さの線であればなんでもokかと思います。  
バッテリケースからユーザインタフェース回路までの電源ケーブルについてはこの回路図に記載がありません。現物に合わせて作成をお願いします。バッテリケースからの電源引き出しのケーブルはAWG24程度の太めの線を使用しました。ポリヒューズが動作する電流でケーブルが過熱しない様にケーブルの電流容量を見積もってください。

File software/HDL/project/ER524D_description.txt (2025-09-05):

Created on: 09/05, 2025
Based on:PhantomDriver

PhantomDriverはこのプロジェクトの元となった回路の名前です。このプロジェクトではそれを変更して流用しているため、名前が残っています。

path_tabel.mifは回路内部のバースト波番号をどの出力チャネル（回路図中の"DRIVE_xx"）に出力するかを指定するためのテーブル(ROMとして展開される)です。
DRIVE_XXのXXから1を引いた値を表のコロンの右側の値として記載してください。
QuartusIDE上では表の形で編集が可能です。
デフォルトでは、SCSIコネクタの1番ピンから順番に24番ピンに向けて順次バースト波が出るように設定されています。
出力しないバースト波番号の信号は"63"(マルチプレクサのハードウエアが実装されていないチャネル)をしてしてください。

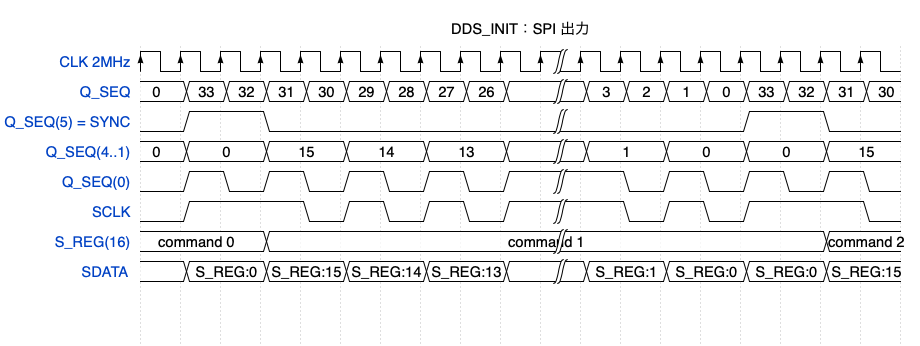
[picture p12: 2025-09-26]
figures/HDL_DDS_INIT_SPI_timing.png

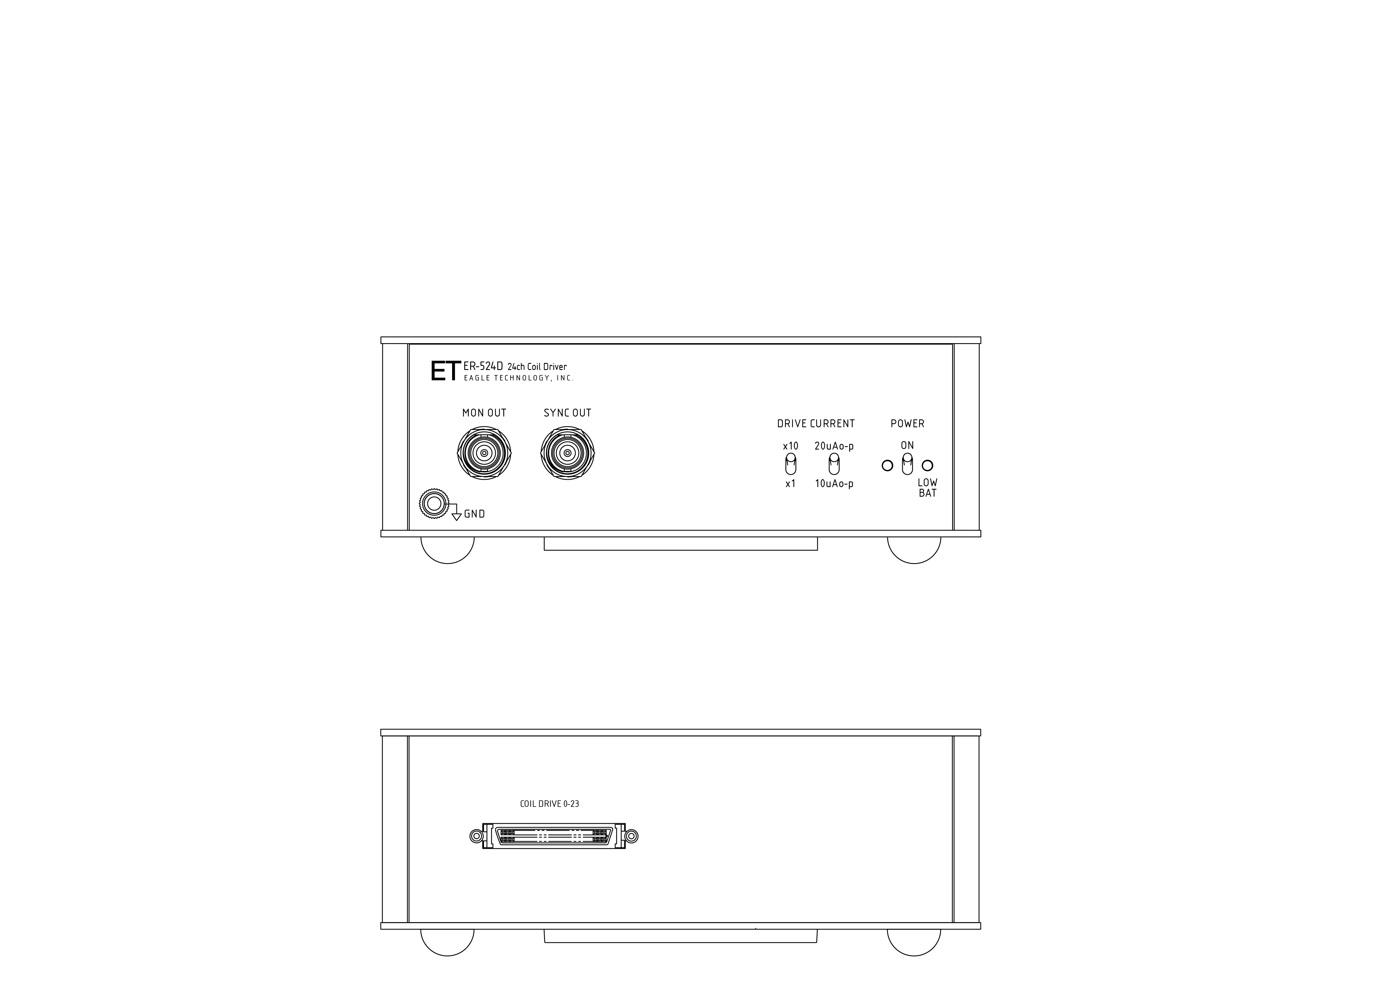
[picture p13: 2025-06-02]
figures/外観図.png

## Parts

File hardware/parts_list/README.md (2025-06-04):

# このディレクトリについて

- このディレクトリに部品表を入れてください。</br>
#プリント基板への部品実装のために必要な部品表と構成部品表が保存されます。</br>
#構成部品表は現状google sheetsで管理されているので、URLリンクをこのreadmeに記入するようにします。</br>

https://docs.google.com/spreadsheets/d/1AgysuI8_JUY7hIKeX8QCyVXA6I_T8JV4ObYrNBxV3HY/edit?usp=sharing

（google sheetsをexcelフォーマットでエクスポートしてもいいが、互換性や保守性が気になるところ）
#
複数の部品表が関連する場合、その関連性（親子関係）をこのREADMEに記述する様にしてください。
VScodeでAscii Tree Generatorを使うと便利です。

例：

## 構成

# [本体](URL)：説明
## [モジュール１](URL):説明
## [モジュール2](URL):説明
### [モジュール2](URL):説明
↑ cmd + shift + P, "Revert Tree String to Text"
↓ 選択ー右クリック "Format Text to Tree String"
.
└── [本体](URL)：説明
    ├── [モジュール１](URL):説明
    └── [モジュール2](URL):説明
        └── [モジュール2](URL):説明

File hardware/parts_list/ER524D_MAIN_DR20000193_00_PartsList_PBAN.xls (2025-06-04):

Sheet: 必ずお読みください
入力項目説明
メ ー カ ー |  |  | 電子部品のメーカー名をご入力ください。
部 品 種 別 |  |  | 電子部品の種別をご入力ください。例：チップ抵抗、トランジスタ、LED、など
電 子 部 品 型 番 |  |  | 電子部品の型番をご入力ください。 ※誤表記による不具合を回避するためにも正確なご入力をお願い致します。 ※表面実装の抵抗やコンデンサ(電解、タンタル以外)は、後述「電子部品見取り表」をご参照のうえ、ご入力ください。
配 置 記 号 / リファレンス |  |  | シルク図/配置図に表記された配置記号/リファレンス番号をご入力ください。 ※複数入力する場合は、カンマ「,」区切りでのご入力をお願い致します。 (入力例)R1～R5、R1-5と略さず、R1,R2,R3,R4,R5とご入力ください。 ※電子部品型番ベースでのご記入をお願い致します。（１つの電子部品型番に対して、配置番号を複数記入）
個 数 |  |  | 電子部品の個数をご入力ください。
ピ ン 数 |  |  | 電子部品の総ピン数をご入力ください。 ※基板取付穴、部品取付穴、全てのスルー・ノンスルーホール、面実装部品のパッド、及び次の①～⑤の配線を伴う箇所（①テストピン、②チェックランド、③引き出しランド、④ジャンパピン、⑤入出力ランドの総計。
実装 / 未実装 |  |  | 実装サービスでの「実装」/「未実装」をご選択ください。 ※同じ電子部品型番の中で実装と未実装が分かれる場合は、それぞれ2行に分けて配置記号をご入力ください。
部品分類 | SMD |  | 表面実装部品
 | DIP |  | 挿入部品
 | 特殊 BGA等 |  | BGA/CSP/LGA/QFNなど部品極性が部品の真下に配置された部品 -BGA：Ball Grid Array/下面に半田ボールの端子を配置したパッケージ。 -CSP：Chip Size Package/チッププサイズと同じか、もしくは僅かに大きいパッケージ。 -LGA：Land Grid Array/裏面に外部入出力用のランドを設けたパッケージ。※BGAの半田ボールがない。 -QFN：Quad Flat Non-Lead Package/QFPに似ていますが、外部入出力用のピンが出ていないパッケージ。
P板.com提供部品 (無料) |  |  | 【無償提供部品一覧】シートに記載されている「メーカー型番」を【部品リスト入力フォーム】シートのD列（電子部品型番）に入力し、I列（実装／未実装）を「実装」に設定いただくと、自動的に「○」が表示されます。 ※無料提供部品：チップコンデンサ/チップ抵抗を約1000種、実装サービスをご利用のお客様に無料提供いたします。 ※「○」が付かない場合は全半角の不一致などにより誤判定されている可能性があります。【無償提供部品一覧】シートより型番をコピー＆ペーストにて【部品リスト入力フォーム】にご入力ください。
 |  |  | http://www.p-ban.com/implementation/chip.html
P板.com調達部品(有料） |  |  | P板.com実装サービスで部品調達を希望される場合に○をご選択ください。 ※調達費用のお見積もりは、部品リストの返却と同時にご連絡いたします。 ※ご希望の納期や市場在庫状況によっては、調達が不可となる部品もございますので、予めご了承ください。
パッケージ情報 部品外形/部品仕様 |  |  | 電子部品のパッケージ情報をご入力ください。例：1608 , DIP , 0.5mmピッチQFP , 0.4mmピッチCN
コ メ ン ト |  |  | 特別なご指示のある電子部品について、自由にご入力ください。 例：未実装挿入穴のマスク処理が必要、など
版、変更履歴 |  |  | 部品種毎に、変更履歴を記載してください。 版は、アカウント登録の版に合わせて記載ください。
調達型式、代替型式 |  |  | 無料提供部品の在庫切れや、正確な調達型式を記載いたします。
部品名称見取り表
1.チップ部品（抵抗、コンデンサ）
 |  |  |  |  | 単位：ｍｍ
 |  |  | 電子部品型番 (C:コンデンサ、R:抵抗） | Ａ寸法 | Ｂ寸法
 |  |  | C/R1608 | 1.6 | 0.8
 |  |  | C/R2125 | 2 | 1.25
 |  |  | C/R3216 | 3.2 | 1.6
 |  |  | C/R3225 | 3.2 | 2.5
 |  |  | C/R4532 | 4.5 | 3.2
2.チップタンタルコンデンサ
 |  |  |  |  | 単位：ｍｍ
 |  |  | 電子部品型番 | Ａ寸法 | Ｂ寸法
 |  |  | CT3216 | 3.2 | 1.6
 |  |  | CT3528 | 3.5 | 2.8
 |  |  | CT4726 | 4.7 | 2.6
 |  |  | CT6032 | 6 | 3.2
 |  |  | CT5846 | 5.8 | 4.6
 |  |  | CT7343 | 7.3 | 4.3
3.チップアルミ電解コンデンサ
 |  |  |  |  |  | 単位：ｍｍ
 |  |  | 電子部品型番 | Ａ寸法 | Ｂ寸法 | C寸法
 |  |  | CE33 | 3.3 | 3.3 | φ3.0
 |  |  | CE43 | 4.3 | 4.3 | φ4.0
 |  |  | CE53 | 5.3 | 5.3 | φ5.0
 |  |  | CE66 | 6.6 | 6.6 | φ6.3
 |  |  | CE83 | 8.3 | 8.3 | φ8.0
 |  |  | CE103 | 10.3 | 10.3 | φ10.0
部品取り付け穴は、ピン数に含めてください。
コネクタの場合 |  |  |  |  |  | トランスの場合
部品リストフォーマット変更履歴
2014-02-01 | v2.0 | 松森 | 部品種別の総計を、直接関数に変更
 |  |  | ピン数合計、実装数合計数量を、直接関数に変更
 |  |  | 部品調達見積欄を修正
2014-03-11 | v2.1 | 松森 | *N列、O列が下の方、"○"選択リスト消えていたのを追加
 |  |  | *縮小しても解像度崩れず文字表示するため、フォントを"Meiryo UI"(Windows 標準添付)に変更
 |  |  | *136行目以降を非表示
 |  |  | *"X"列にリストを埋め込み
2014-06-12 | v2.2 | 松森 | *固定行を変更
 |  |  | *在庫状況列に条件付き書式設定
 |  |  | *その他各種バグ修正
2015-03-31 | V2.3 | 松森 | *無償提供部品を記載すると、無償提供部品欄に自動で"○"が表示されるよう条件式を挿入
 |  |  | *併せて、無償提供部品参照用一覧シートの作成・追加
 |  |  | *最小購入数が必要数量を下回る場合、セルを赤色にハッチングする
 |  |  | *シート1の名称変更
 |  |  | *変更履歴シートの追加
2015-06-19 | v2.4 | 松森 | ・ゼロΩ抵抗を無償対象に追加
 |  |  | ・変更履歴の列を追加し、変更履歴シートを削除
 |  |  | ・その他書式、印刷機能の変更
 |  |  | ・無償提供部品の入れ替え
2015-08-14 | v2.5 | 松森 | ・ゼロΩ抵抗の無償対象品が正しく反映されていなかったバグ修正
 |  |  | ・フォームへバージョン情報を埋め込み
2015-11-05 | v2.6 | 上田 | ・無償提供部品(RK73H2ATTD1601F)の抵抗値を正しい値に修正
2015-11-09 | v2.7 | 上田 | ・P板.com調達部品(無料)欄のフォントを変更
2016-01-15 | v2.8 | 箕浦 | ・無償提供部品一覧の「GRM32NF11E106Z」を削除
 |  |  | ・部品リスト入力フォームの4行目F列～L列の計算式が136行目以降を対象としていなかった不具合を修正
2016-01-27 | v2.9 | 箕浦 | ・「無償提供部品一覧」シートの表記修正
2016-08-26 | v2.10 | 松森 | ・「GRM31CF11E106Z」の許容差値修正
2016-11-15 | v2.11 | 松森 | ・部品調達欄表示順序変更
 |  |  | ・備考欄、荷姿欄追加
 |  |  | ・在庫状況のリスト微修正
2017-03-21 | v2.12 | 松森 | ・調達金額合計欄作成
 |  |  | ・在庫状況「長納期」を追加
 |  |  | ・その他微修正
2017-06-29 | v2.13 | 松森 | ・村田製3216サイズ以上のチップコンの取扱い中止
2017-07-19 | V2.14 | 松森 | ・KOA製1005サイズの定格電力を0.1Wに変更
 |  |  | (2015年10月のKOA仕様変更に伴う)
2017-09-14 | v2.15 | 松森 | ・KOA製2012サイズの定格電力を0.25Wへ変更
 |  |  | ・KOA製1608サイズ、1K以下の定格電力を0.125Wへ変更
 |  |  | ・MURATA製一部型式、許容差および定格修正
 |  |  | ・MURATA製一部部品削除
 |  |  | ・その他書式設定等微修正
2017-10-12 | v2.20 | 松森 | ・部品調達関連項目の移動
 |  |  | ・条件付き書式追加
2018-06-22 | v2.31 | 松森 | ・「1608」サイズと「2012」サイズのチップコンデンサを無償対象品から除外
2018-10-18 | V2.32 | 山田 | ・部品調達関連項目追加（条件付き書式追加/在庫状況：在庫少追加）
 |  |  | ・「必ずお読みください」シートの「配置記号 / リファレンス」の項目修正（配置記号の省略について）
2019-09-05 | V2.4 | 岡田 | Excelファイル名を部品表内に表記する関数追加
 |  |  | 無償提供部品型番入力後にスペースが入るとO列に丸がされない問題を修正
2019-09-10 | V2.41 | 岡田 | "AD"列にトレイ追加

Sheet: 部品リスト入力フォーム
partslist(Rev,2.41) |  |  | 電 子 部 品 型 番 ※半角英数字 ※サフィックスまで入力必須 | 配 置 記 号 リ フ ァ レ ン ス ※半角英数字） | 個数 | ピ ン 数 (部品取付穴 を含む） |  | 実装/ 未実装 | 部 品 分 類 |  |  | 必要数 実装枚数を入れてください。 ↓ | P板.com 提供 部品 (無料) | P板.com 調達 部品 (有料） | パッケージ情報 部品外形/部品仕様 | コ メ ン ト ※未実装挿入穴のマスク 処理が必要、など | 版 変更履歴 | 入荷数 | 返却
ER524D_MAIN_DR20000193_00_PartsList_PBAN.xls
No | メーカー | 部品種別 |  |  |  | 1個 あたり | 合計 | 実装個数 | SMD | DIP | 特殊 BGA等 |  |  |  |  |  |  |  |  | P板.com部品調達使用欄
 |  |  |  |  | 171 | 376 | 731 | 170 | 147 | 23 | 0 | 3 | リスト (http://www.p-ban.com/implementation/chip.html)
例 | KOA | チップ抵抗 | RK73B2ATTD1002F | R1,R5,R9,R10 | 4 | 2 | 8 | 未実装 | SMD |  |  |  |  |  | 2012 |  | 4版 型式訂正、個数変更、 実装→未実装へ |  |  | 必要数 | 調達数 | 在庫状況 | メーカ | 調達品番 | 荷姿 | 納期 | 備考
1 □ | AD | 差動アンプ | AD8227ARZ | U11 | 1 | 8 | 8 | 実装 | SMD |  |  | 3 |  |  |  |  |  |  | □
2 □ | AKIZUKI | 2列ピンヘッダ | PH-2x5SG | CN18 | 1 | 10 | 10 | 実装 | DIP |  |  | 3 |  |  |  |  |  |  | □
3 □ | AKIZUKI | 2列ピンソケット | C-00169 | CN19 | 1 | 14 | 14 | 実装 | DIP |  |  | 3 |  |  |  |  |  |  | □
4 □ | ALPHA | 精密抵抗 | FLCX100R00A | R56 | 1 | 2 | 2 | 実装 | DIP |  |  | 3 |  |  |  |  |  |  | □
5 □ | ALTERA | CPLD | 5M160ZT100A5N | U27 | 1 | 100 | 100 | 実装 | SMD |  |  | 3 |  |  |  |  |  |  | □
6 □ | HIROSE | DF11コネクタ(PLUG) | DF11-4DP-2DSA(24) | CN1, CN2, CN3, CN4 | 4 | 4 | 16 | 実装 | DIP |  |  | 12 |  |  |  |  |  |  | □
7 □ | HIROSE | DF11コネクタ(PLUG) | DF11-14DP-2DSA(24) | CN20 | 1 | 14 | 14 | 実装 | DIP |  |  | 3 |  |  |  |  |  |  | □
8 □ | HIROSUGI | 取り付けスペーサ | VAB-3-10 | M1 | 1 | 1 | 1 | 未実装 | DIP |  |  | 0 |  |  |  |  |  |  | □
9 □ | HONDA | ハーフピッチSCSIコネクタ | PCS-XE50LFD+ | CN16 | 1 | 52 | 52 | 実装 | DIP |  |  | 3 |  |  |  |  |  |  | □
10 □ | JRC | コンパレータ | NJU7108F3 | U7 | 1 | 5 | 5 | 実装 | SMD |  |  | 3 |  |  |  |  |  |  | □
11 □ | KOA | 厚膜チップ抵抗 | RK73H1JTTD1001F | R65, R67, R68, R69, R70, R71, R83 | 7 | 2 | 14 | 実装 | SMD |  |  | 21 | ○ |  |  |  |  |  | □
12 □ | KOA | 厚膜チップ抵抗 | RK73H1JTTD1004F | R34 | 1 | 2 | 2 | 実装 | SMD |  |  | 3 | ○ |  |  |  |  |  | □
13 □ | KOA | 厚膜チップ抵抗 | RK73H1JTTD1003F | R26, R36, R64, R72, R73, R74, R75, R76, R77 | 9 | 2 | 18 | 実装 | SMD |  |  | 27 | ○ |  |  |  |  |  | □
14 □ | KOA | 厚膜チップ抵抗 | RK73Z1JTTD | R22, R27, R28, R33, R35 | 5 | 2 | 10 | 実装 | SMD |  |  | 15 | ○ |  |  |  |  |  | □
15 □ | KOA | 厚膜チップ抵抗 | RK73H1JTTD47R0F | R18, R39 | 2 | 2 | 4 | 実装 | SMD |  |  | 6 | ○ |  |  |  |  |  | □
16 □ | KOA | 厚膜チップ抵抗 | RK73H1JTTD30R0F | R46 | 1 | 2 | 2 | 実装 | SMD |  |  | 3 | ○ |  |  |  |  |  | □
17 □ | KOA | 厚膜チップ抵抗 | RK73H1JTTD1002F | R63, R66 | 2 | 2 | 4 | 実装 | SMD |  |  | 6 | ○ |  |  |  |  |  | □
18 □ | KOA | 厚膜チップ抵抗 | RK73H1JTTD2002F | R78, R79, R80, R81, R82 | 5 | 2 | 10 | 実装 | SMD |  |  | 15 | ○ |  |  |  |  |  | □
19 □ | KOA | 厚膜チップ抵抗 | RK73H1JTTD2001F | R84 | 1 | 2 | 2 | 実装 | SMD |  |  | 3 | ○ |  |  |  |  |  | □
20 □ | KOA | 厚膜チップ抵抗 | RK73H1JTTD6200F | R58 | 1 | 2 | 2 | 実装 | SMD |  |  | 3 | ○ |  |  |  |  |  | □
21 □ | MAC8 | テストポイント | LC-33-G | TP1, TP2, TP3, TP4, TP5, TP6, TP7, TP8, TP9, TP15 | 10 | 1 | 10 | 実装 | DIP |  |  | 30 |  |  |  |  |  |  | □
22 □ | MAXIM | アナログMPX | MAX4617CUE+ | U12, U14, U16, U18, U20, U22, U23, U25 | 8 | 16 | 128 | 実装 | SMD |  |  | 24 |  |  |  |  |  |  | □
23 □ | Panasonic | アルミ固体コンデンサ | 10SEP56M | C8, C23, C46 | 3 | 2 | 6 | 実装 | DIP |  |  | 9 |  |  |  |  |  |  | □
24 □ | SSM | 薄膜チップ抵抗 | RG1608N-153-W | R57 | 1 | 2 | 2 | 実装 | SMD |  |  | 3 |  |  |  |  |  |  | □
25 □ | SSM | 薄膜チップ抵抗 | RG1608N-202-W | R55 | 1 | 2 | 2 | 実装 | SMD |  |  | 3 |  |  |  |  |  |  | □
26 □ | SSM | 薄膜チップ抵抗 | RR0816P-393-D | R50 | 1 | 2 | 2 | 実装 | SMD |  |  | 3 |  |  |  |  |  |  | □
27 □ | SSM | 薄膜チップ抵抗 | RR0816P-562-D | R49 | 1 | 2 | 2 | 実装 | SMD |  |  | 3 |  |  |  |  |  |  | □
28 □ | SSM | 薄膜チップ抵抗 | RR0816P-683-D | R42, R43 | 2 | 2 | 4 | 実装 | SMD |  |  | 6 |  |  |  |  |  |  | □
29 □ | SSM | 薄膜チップ抵抗 | RR0816P-912-D | R23 | 1 | 2 | 2 | 実装 | SMD |  |  | 3 |  |  |  |  |  |  | □
30 □ | SSM | 薄膜チップ抵抗 | RR0816P-113-D | R25 | 1 | 2 | 2 | 実装 | SMD |  |  | 3 |  |  |  |  |  |  | □
31 □ | SSM | 薄膜チップ抵抗 | RR0816P-114-D | R24 | 1 | 2 | 2 | 実装 | SMD |  |  | 3 |  |  |  |  |  |  | □
32 □ | SSM | 薄膜チップ抵抗 | RR0816P-103-D | R20, R29, R53, R54 | 4 | 2 | 8 | 実装 | SMD |  |  | 12 |  |  |  |  |  |  | □
33 □ | SSM | 薄膜チップ抵抗 | RR0816P-513-D | R8, R9, R10, R11, R13, R14, R15, R16, R21, R30, R31, R32, R37, R38, R40, R41, R44, R45 | 18 | 2 | 36 | 実装 | SMD |  |  | 54 |  |  |  |  |  |  | □
34 □ | SSM | 薄膜チップ抵抗 | RR0816P-104-D | R47, R48, R51, R52 | 4 | 2 | 8 | 実装 | SMD |  |  | 12 |  |  |  |  |  |  | □
35 □ | TDK | コモンモードチョーク | ACM4520-142-2P | L1, L2, L3, L4, L5 | 5 | 4 | 20 | 実装 | SMD |  |  | 15 |  |  |  |  |  |  | □
36 □ | TDK | 積層セラミックコンデンサ | C2012JB1E106K | C57 | 1 | 2 | 2 | 実装 | SMD |  |  | 3 |  |  |  |  |  |  | □
37 □ | TDK | 積層セラミックコンデンサ | CGA3E3X5R1E105K | C20, C26, C58, C59, C60, C61, C62 | 7 | 2 | 14 | 実装 | SMD |  |  | 21 |  |  |  |  |  |  | □
38 □ | TE | ポリスイッチ | RXEF050 | F1 | 1 | 2 | 2 | 実装 | DIP |  |  | 3 |  |  |  |  |  |  | □
39 □ | TI | 電圧レギュレータ | TPS79933DDC | U4, U26 | 2 | 5 | 10 | 実装 | SMD |  |  | 6 |  |  |  |  |  |  | □
40 □ | TI | オペアンプ | OPA2314AIDGK | U8 | 1 | 8 | 8 | 実装 | SMD |  |  | 3 |  |  |  |  |  |  | □
41 □ | TI | 電圧レギュレータ | TPS79918DDC | U28 | 1 | 5 | 5 | 実装 | SMD |  |  | 3 |  |  |  |  |  |  | □
42 □ | TI | オペアンプ | OPA2344EA | U2, U5 | 2 | 8 | 16 | 実装 | SMD |  |  | 6 |  |  |  |  |  |  | □
43 □ | TI | アナログスイッチ | TS5A23159DGS | U3, U9 | 2 | 10 | 20 | 実装 | SMD |  |  | 6 |  |  |  |  |  |  | □
44 □ | TI | 電圧監視 | TPS3808G01DBV | U6 | 1 | 6 | 6 | 実装 | SMD |  |  | 3 |  |  |  |  |  |  | □
45 □ | TOSHIBA | C-MOS | TC74VHC4052AFT | U10 | 1 | 16 | 16 | 実装 | SMD |  |  | 3 |  |  |  |  |  |  | □
46 □ | TOSHIBA | フォトカプラ | TLP291(GR,SE | U30 | 1 | 4 | 4 | 実装 | SMD |  |  | 3 |  |  |  |  |  |  | □
47 □ | TOSHIBA | ショットキーダイオード | 1SS372 | D1, D2 | 2 | 3 | 6 | 実装 | SMD |  |  | 6 |  |  |  |  |  |  | □
48 □ | TOSHIBA | C-MOS | 74VHC9541FT | U29 | 1 | 20 | 20 | 実装 | SMD |  |  | 3 |  |  |  |  |  |  | □
49 □ | 太陽誘電 | 積層セラミックコンデンサ | TMK212ABJ475KG-T | C13, C53 | 2 | 2 | 4 | 実装 | SMD |  |  | 6 |  |  |  |  |  |  | □
50 □ | 村田製作所 | 積層セラミックコンデンサ | GRM1882C1H222J | C19 | 1 | 2 | 2 | 実装 | SMD |  |  | 3 |  |  |  |  |  |  | □
51 □ | 村田製作所 | 積層セラミックコンデンサ | GRM2162C1H472J | C17 | 1 |  | 0 | 実装 | SMD |  |  | 3 |  |  |  |  |  |  | □
52 □ | 村田製作所 | 積層セラミックコンデンサ | GRM2192C1H103J | C12, C52, C56 | 3 | 2 | 6 | 実装 | SMD |  |  | 9 |  |  |  |  |  |  | □
53 □ | 村田製作所 | 積層セラミックコンデンサ | GRM155B31C104K | C9, C10, C11, C15, C16, C18, C21, C24, C25, C27, C28, C30, C32, C34, C36, C38, C39, C41, C42, C43, C44, C45, C47, C48, C49, C50, C51, C54, C55 | 29 | 2 | 58 | 実装 | SMD |  |  | 87 | ○ |  |  |  |  |  | □
54 □ | 村田製作所 | 積層セラミックコンデンサ | GRM1882C1H332J | C3, C4, C5, C7 | 4 | 2 | 8 | 実装 | SMD |  |  | 12 |  |  |  |  |  |  | □
55 □ |  |  |  |  |  |  |  |  |  |  |  |  |  |  |  |  |  |  | □
56 □ |  |  |  |  |  |  |  |  |  |  |  |  |  |  |  |  |  |  | □
57 □ |  |  |  |  |  |  |  |  |  |  |  |  |  |  |  |  |  |  | □
58 □ |  |  |  |  |  |  |  |  |  |  |  |  |  |  |  |  |  |  | □
59 □ |  |  |  |  |  |  |  |  |  |  |  |  |  |  |  |  |  |  | □
60 □ |  |  |  |  |  |  |  |  |  |  |  |  |  |  |  |  |  |  | □
61 □ |  |  |  |  |  |  |  |  |  |  |  |  |  |  |  |  |  |  | □
62 □ |  |  |  |  |  |  |  |  |  |  |  |  |  |  |  |  |  |  | □
63 □ |  |  |  |  |  |  |  |  |  |  |  |  |  |  |  |  |  |  | □
64 □ |  |  |  |  |  |  |  |  |  |  |  |  |  |  |  |  |  |  | □
65 □ |  |  |  |  |  |  |  |  |  |  |  |  |  |  |  |  |  |  | □
66 □ |  |  |  |  |  |  |  |  |  |  |  |  |  |  |  |  |  |  | □
67 □ |  |  |  |  |  |  |  |  |  |  |  |  |  |  |  |  |  |  | □
68 □ |  |  |  |  |  |  |  |  |  |  |  |  |  |  |  |  |  |  | □
69 □ |  |  |  |  |  |  |  |  |  |  |  |  |  |  |  |  |  |  | □
70 □ |  |  |  |  |  |  |  |  |  |  |  |  |  |  |  |  |  |  | □
71 □ |  |  |  |  |  |  |  |  |  |  |  |  |  |  |  |  |  |  | □
72 □ |  |  |  |  |  |  |  |  |  |  |  |  |  |  |  |  |  |  | □
73 □ |  |  |  |  |  |  |  |  |  |  |  |  |  |  |  |  |  |  | □
74 □ |  |  |  |  |  |  |  |  |  |  |  |  |  |  |  |  |  |  | □
75 □ |  |  |  |  |  |  |  |  |  |  |  |  |  |  |  |  |  |  | □
76 □ |  |  |  |  |  |  |  |  |  |  |  |  |  |  |  |  |  |  | □
77 □ |  |  |  |  |  |  |  |  |  |  |  |  |  |  |  |  |  |  | □
78 □ |  |  |  |  |  |  |  |  |  |  |  |  |  |  |  |  |  |  | □
79 □ |  |  |  |  |  |  |  |  |  |  |  |  |  |  |  |  |  |  | □
80 □ |  |  |  |  |  |  |  |  |  |  |  |  |  |  |  |  |  |  | □
81 □ |  |  |  |  |  |  |  |  |  |  |  |  |  |  |  |  |  |  | □
82 □ |  |  |  |  |  |  |  |  |  |  |  |  |  |  |  |  |  |  | □
83 □ |  |  |  |  |  |  |  |  |  |  |  |  |  |  |  |  |  |  | □
84 □ |  |  |  |  |  |  |  |  |  |  |  |  |  |  |  |  |  |  | □
85 □ |  |  |  |  |  |  |  |  |  |  |  |  |  |  |  |  |  |  | □
86 □ |  |  |  |  |  |  |  |  |  |  |  |  |  |  |  |  |  |  | □
87 □ |  |  |  |  |  |  |  |  |  |  |  |  |  |  |  |  |  |  | □
88 □ |  |  |  |  |  |  |  |  |  |  |  |  |  |  |  |  |  |  | □
89 □ |  |  |  |  |  |  |  |  |  |  |  |  |  |  |  |  |  |  | □
90 □ |  |  |  |  |  |  |  |  |  |  |  |  |  |  |  |  |  |  | □
91 □ |  |  |  |  |  |  |  |  |  |  |  |  |  |  |  |  |  |  | □
92 □ |  |  |  |  |  |  |  |  |  |  |  |  |  |  |  |  |  |  | □
93 □ |  |  |  |  |  |  |  |  |  |  |  |  |  |  |  |  |  |  | □
94 □ |  |  |  |  |  |  |  |  |  |  |  |  |  |  |  |  |  |  | □
95 □ |  |  |  |  |  |  |  |  |  |  |  |  |  |  |  |  |  |  | □
96 □ |  |  |  |  |  |  |  |  |  |  |  |  |  |  |  |  |  |  | □
97 □ |  |  |  |  |  |  |  |  |  |  |  |  |  |  |  |  |  |  | □
98 □ |  |  |  |  |  |  |  |  |  |  |  |  |  |  |  |  |  |  | □
99 □ |  |  |  |  |  |  |  |  |  |  |  |  |  |  |  |  |  |  | □
100 □ |  |  |  |  |  |  |  |  |  |  |  |  |  |  |  |  |  |  | □
101 □ |  |  |  |  |  |  |  |  |  |  |  |  |  |  |  |  |  |  | □
102 □ |  |  |  |  |  |  |  |  |  |  |  |  |  |  |  |  |  |  | □
103 □ |  |  |  |  |  |  |  |  |  |  |  |  |  |  |  |  |  |  | □
104 □ |  |  |  |  |  |  |  |  |  |  |  |  |  |  |  |  |  |  | □
105 □ |  |  |  |  |  |  |  |  |  |  |  |  |  |  |  |  |  |  | □
106 □ |  |  |  |  |  |  |  |  |  |  |  |  |  |  |  |  |  |  | □
107 □ |  |  |  |  |  |  |  |  |  |  |  |  |  |  |  |  |  |  | □
108 □ |  |  |  |  |  |  |  |  |  |  |  |  |  |  |  |  |  |  | □
109 □ |  |  |  |  |  |  |  |  |  |  |  |  |  |  |  |  |  |  | □
110 □ |  |  |  |  |  |  |  |  |  |  |  |  |  |  |  |  |  |  | □
111 □ |  |  |  |  |  |  |  |  |  |  |  |  |  |  |  |  |  |  | □
112 □ |  |  |  |  |  |  |  |  |  |  |  |  |  |  |  |  |  |  | □
113 □ |  |  |  |  |  |  |  |  |  |  |  |  |  |  |  |  |  |  | □
114 □ |  |  |  |  |  |  |  |  |  |  |  |  |  |  |  |  |  |  | □
115 □ |  |  |  |  |  |  |  |  |  |  |  |  |  |  |  |  |  |  | □
116 □ |  |  |  |  |  |  |  |  |  |  |  |  |  |  |  |  |  |  | □
117 □ |  |  |  |  |  |  |  |  |  |  |  |  |  |  |  |  |  |  | □
118 □ |  |  |  |  |  |  |  |  |  |  |  |  |  |  |  |  |  |  | □
119 □ |  |  |  |  |  |  |  |  |  |  |  |  |  |  |  |  |  |  | □
120 □ |  |  |  |  |  |  |  |  |  |  |  |  |  |  |  |  |  |  | □
121 □ |  |  |  |  |  |  |  |  |  |  |  |  |  |  |  |  |  |  | □
122 □ |  |  |  |  |  |  |  |  |  |  |  |  |  |  |  |  |  |  | □
123 □ |  |  |  |  |  |  |  |  |  |  |  |  |  |  |  |  |  |  | □
124 □ |  |  |  |  |  |  |  |  |  |  |  |  |  |  |  |  |  |  | □
125 □ |  |  |  |  |  |  |  |  |  |  |  |  |  |  |  |  |  |  | □
126 □ |  |  |  |  |  |  |  |  |  |  |  |  |  |  |  |  |  |  | □
127 □ |  |  |  |  |  |  |  |  |  |  |  |  |  |  |  |  |  |  | □
128 □ |  |  |  |  |  |  |  |  |  |  |  |  |  |  |  |  |  |  | □
129 □ |  |  |  |  |  |  |  |  |  |  |  |  |  |  |  |  |  |  | □
130 □ |  |  |  |  |  |  |  |  |  |  |  |  |  |  |  |  |  |  | □
131 □ |  |  |  |  |  |  |  |  |  |  |  |  |  |  |  |  |  |  | □
132 □ |  |  |  |  |  |  |  |  |  |  |  |  |  |  |  |  |  |  | □
133 □ |  |  |  |  |  |  |  |  |  |  |  |  |  |  |  |  |  |  | □
134 □ |  |  |  |  |  |  |  |  |  |  |  |  |  |  |  |  |  |  | □
135 □ |  |  |  |  |  |  |  |  |  |  |  |  |  |  |  |  |  |  | □
136 □ |  |  |  |  |  |  |  |  |  |  |  |  |  |  |  |  |  |  | □
137 □ |  |  |  |  |  |  |  |  |  |  |  |  |  |  |  |  |  |  | □
138 □ |  |  |  |  |  |  |  |  |  |  |  |  |  |  |  |  |  |  | □
139 □ |  |  |  |  |  |  |  |  |  |  |  |  |  |  |  |  |  |  | □
140 □ |  |  |  |  |  |  |  |  |  |  |  |  |  |  |  |  |  |  | □
141 □ |  |  |  |  |  |  |  |  |  |  |  |  |  |  |  |  |  |  | □
142 □ |  |  |  |  |  |  |  |  |  |  |  |  |  |  |  |  |  |  | □
143 □ |  |  |  |  |  |  |  |  |  |  |  |  |  |  |  |  |  |  | □
144 □ |  |  |  |  |  |  |  |  |  |  |  |  |  |  |  |  |  |  | □
145 □ |  |  |  |  |  |  |  |  |  |  |  |  |  |  |  |  |  |  | □
146 □ |  |  |  |  |  |  |  |  |  |  |  |  |  |  |  |  |  |  | □
147 □ |  |  |  |  |  |  |  |  |  |  |  |  |  |  |  |  |  |  | □
148 □ |  |  |  |  |  |  |  |  |  |  |  |  |  |  |  |  |  |  | □
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

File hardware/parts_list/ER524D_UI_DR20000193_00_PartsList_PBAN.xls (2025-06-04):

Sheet: 必ずお読みください
入力項目説明
メ ー カ ー |  |  | 電子部品のメーカー名をご入力ください。
部 品 種 別 |  |  | 電子部品の種別をご入力ください。例：チップ抵抗、トランジスタ、LED、など
電 子 部 品 型 番 |  |  | 電子部品の型番をご入力ください。 ※誤表記による不具合を回避するためにも正確なご入力をお願い致します。 ※表面実装の抵抗やコンデンサ(電解、タンタル以外)は、後述「電子部品見取り表」をご参照のうえ、ご入力ください。
配 置 記 号 / リファレンス |  |  | シルク図/配置図に表記された配置記号/リファレンス番号をご入力ください。 ※複数入力する場合は、カンマ「,」区切りでのご入力をお願い致します。 (入力例)R1～R5、R1-5と略さず、R1,R2,R3,R4,R5とご入力ください。 ※電子部品型番ベースでのご記入をお願い致します。（１つの電子部品型番に対して、配置番号を複数記入）
個 数 |  |  | 電子部品の個数をご入力ください。
ピ ン 数 |  |  | 電子部品の総ピン数をご入力ください。 ※基板取付穴、部品取付穴、全てのスルー・ノンスルーホール、面実装部品のパッド、及び次の①～⑤の配線を伴う箇所（①テストピン、②チェックランド、③引き出しランド、④ジャンパピン、⑤入出力ランドの総計。
実装 / 未実装 |  |  | 実装サービスでの「実装」/「未実装」をご選択ください。 ※同じ電子部品型番の中で実装と未実装が分かれる場合は、それぞれ2行に分けて配置記号をご入力ください。
部品分類 | SMD |  | 表面実装部品
 | DIP |  | 挿入部品
 | 特殊 BGA等 |  | BGA/CSP/LGA/QFNなど部品極性が部品の真下に配置された部品 -BGA：Ball Grid Array/下面に半田ボールの端子を配置したパッケージ。 -CSP：Chip Size Package/チッププサイズと同じか、もしくは僅かに大きいパッケージ。 -LGA：Land Grid Array/裏面に外部入出力用のランドを設けたパッケージ。※BGAの半田ボールがない。 -QFN：Quad Flat Non-Lead Package/QFPに似ていますが、外部入出力用のピンが出ていないパッケージ。
P板.com提供部品 (無料) |  |  | 【無償提供部品一覧】シートに記載されている「メーカー型番」を【部品リスト入力フォーム】シートのD列（電子部品型番）に入力し、I列（実装／未実装）を「実装」に設定いただくと、自動的に「○」が表示されます。 ※無料提供部品：チップコンデンサ/チップ抵抗を約1000種、実装サービスをご利用のお客様に無料提供いたします。 ※「○」が付かない場合は全半角の不一致などにより誤判定されている可能性があります。【無償提供部品一覧】シートより型番をコピー＆ペーストにて【部品リスト入力フォーム】にご入力ください。
 |  |  | http://www.p-ban.com/implementation/chip.html
P板.com調達部品(有料） |  |  | P板.com実装サービスで部品調達を希望される場合に○をご選択ください。 ※調達費用のお見積もりは、部品リストの返却と同時にご連絡いたします。 ※ご希望の納期や市場在庫状況によっては、調達が不可となる部品もございますので、予めご了承ください。
パッケージ情報 部品外形/部品仕様 |  |  | 電子部品のパッケージ情報をご入力ください。例：1608 , DIP , 0.5mmピッチQFP , 0.4mmピッチCN
コ メ ン ト |  |  | 特別なご指示のある電子部品について、自由にご入力ください。 例：未実装挿入穴のマスク処理が必要、など
版、変更履歴 |  |  | 部品種毎に、変更履歴を記載してください。 版は、アカウント登録の版に合わせて記載ください。
調達型式、代替型式 |  |  | 無料提供部品の在庫切れや、正確な調達型式を記載いたします。
部品名称見取り表
1.チップ部品（抵抗、コンデンサ）
 |  |  |  |  | 単位：ｍｍ
 |  |  | 電子部品型番 (C:コンデンサ、R:抵抗） | Ａ寸法 | Ｂ寸法
 |  |  | C/R1608 | 1.6 | 0.8
 |  |  | C/R2125 | 2 | 1.25
 |  |  | C/R3216 | 3.2 | 1.6
 |  |  | C/R3225 | 3.2 | 2.5
 |  |  | C/R4532 | 4.5 | 3.2
2.チップタンタルコンデンサ
 |  |  |  |  | 単位：ｍｍ
 |  |  | 電子部品型番 | Ａ寸法 | Ｂ寸法
 |  |  | CT3216 | 3.2 | 1.6
 |  |  | CT3528 | 3.5 | 2.8
 |  |  | CT4726 | 4.7 | 2.6
 |  |  | CT6032 | 6 | 3.2
 |  |  | CT5846 | 5.8 | 4.6
 |  |  | CT7343 | 7.3 | 4.3
3.チップアルミ電解コンデンサ
 |  |  |  |  |  | 単位：ｍｍ
 |  |  | 電子部品型番 | Ａ寸法 | Ｂ寸法 | C寸法
 |  |  | CE33 | 3.3 | 3.3 | φ3.0
 |  |  | CE43 | 4.3 | 4.3 | φ4.0
 |  |  | CE53 | 5.3 | 5.3 | φ5.0
 |  |  | CE66 | 6.6 | 6.6 | φ6.3
 |  |  | CE83 | 8.3 | 8.3 | φ8.0
 |  |  | CE103 | 10.3 | 10.3 | φ10.0
部品取り付け穴は、ピン数に含めてください。
コネクタの場合 |  |  |  |  |  | トランスの場合
部品リストフォーマット変更履歴
2014-02-01 | v2.0 | 松森 | 部品種別の総計を、直接関数に変更
 |  |  | ピン数合計、実装数合計数量を、直接関数に変更
 |  |  | 部品調達見積欄を修正
2014-03-11 | v2.1 | 松森 | *N列、O列が下の方、"○"選択リスト消えていたのを追加
 |  |  | *縮小しても解像度崩れず文字表示するため、フォントを"Meiryo UI"(Windows 標準添付)に変更
 |  |  | *136行目以降を非表示
 |  |  | *"X"列にリストを埋め込み
2014-06-12 | v2.2 | 松森 | *固定行を変更
 |  |  | *在庫状況列に条件付き書式設定
 |  |  | *その他各種バグ修正
2015-03-31 | V2.3 | 松森 | *無償提供部品を記載すると、無償提供部品欄に自動で"○"が表示されるよう条件式を挿入
 |  |  | *併せて、無償提供部品参照用一覧シートの作成・追加
 |  |  | *最小購入数が必要数量を下回る場合、セルを赤色にハッチングする
 |  |  | *シート1の名称変更
 |  |  | *変更履歴シートの追加
2015-06-19 | v2.4 | 松森 | ・ゼロΩ抵抗を無償対象に追加
 |  |  | ・変更履歴の列を追加し、変更履歴シートを削除
 |  |  | ・その他書式、印刷機能の変更
 |  |  | ・無償提供部品の入れ替え
2015-08-14 | v2.5 | 松森 | ・ゼロΩ抵抗の無償対象品が正しく反映されていなかったバグ修正
 |  |  | ・フォームへバージョン情報を埋め込み
2015-11-05 | v2.6 | 上田 | ・無償提供部品(RK73H2ATTD1601F)の抵抗値を正しい値に修正
2015-11-09 | v2.7 | 上田 | ・P板.com調達部品(無料)欄のフォントを変更
2016-01-15 | v2.8 | 箕浦 | ・無償提供部品一覧の「GRM32NF11E106Z」を削除
 |  |  | ・部品リスト入力フォームの4行目F列～L列の計算式が136行目以降を対象としていなかった不具合を修正
2016-01-27 | v2.9 | 箕浦 | ・「無償提供部品一覧」シートの表記修正
2016-08-26 | v2.10 | 松森 | ・「GRM31CF11E106Z」の許容差値修正
2016-11-15 | v2.11 | 松森 | ・部品調達欄表示順序変更
 |  |  | ・備考欄、荷姿欄追加
 |  |  | ・在庫状況のリスト微修正
2017-03-21 | v2.12 | 松森 | ・調達金額合計欄作成
 |  |  | ・在庫状況「長納期」を追加
 |  |  | ・その他微修正
2017-06-29 | v2.13 | 松森 | ・村田製3216サイズ以上のチップコンの取扱い中止
2017-07-19 | V2.14 | 松森 | ・KOA製1005サイズの定格電力を0.1Wに変更
 |  |  | (2015年10月のKOA仕様変更に伴う)
2017-09-14 | v2.15 | 松森 | ・KOA製2012サイズの定格電力を0.25Wへ変更
 |  |  | ・KOA製1608サイズ、1K以下の定格電力を0.125Wへ変更
 |  |  | ・MURATA製一部型式、許容差および定格修正
 |  |  | ・MURATA製一部部品削除
 |  |  | ・その他書式設定等微修正
2017-10-12 | v2.20 | 松森 | ・部品調達関連項目の移動
 |  |  | ・条件付き書式追加
2018-06-22 | v2.31 | 松森 | ・「1608」サイズと「2012」サイズのチップコンデンサを無償対象品から除外
2018-10-18 | V2.32 | 山田 | ・部品調達関連項目追加（条件付き書式追加/在庫状況：在庫少追加）
 |  |  | ・「必ずお読みください」シートの「配置記号 / リファレンス」の項目修正（配置記号の省略について）
2019-09-05 | V2.4 | 岡田 | Excelファイル名を部品表内に表記する関数追加
 |  |  | 無償提供部品型番入力後にスペースが入るとO列に丸がされない問題を修正
2019-09-10 | V2.41 | 岡田 | "AD"列にトレイ追加

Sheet: 部品リスト入力フォーム
partslist(Rev,2.41) |  |  | 電 子 部 品 型 番 ※半角英数字 ※サフィックスまで入力必須 | 配 置 記 号 リ フ ァ レ ン ス ※半角英数字） | 個数 | ピ ン 数 (部品取付穴 を含む） |  | 実装/ 未実装 | 部 品 分 類 |  |  | 必要数 実装枚数を入れてください。 ↓ | P板.com 提供 部品 (無料) | P板.com 調達 部品 (有料） | パッケージ情報 部品外形/部品仕様 | コ メ ン ト ※未実装挿入穴のマスク 処理が必要、など | 版 変更履歴 | 入荷数 | 返却
ER524D_UI_DR20000193_00_PartsList_PBAN.xls
No | メーカー | 部品種別 |  |  |  | 1個 あたり | 合計 | 実装個数 | SMD | DIP | 特殊 BGA等 |  |  |  |  |  |  |  |  | P板.com部品調達使用欄
 |  |  |  |  | 18 | 46 | 69 | 16 | 0 | 16 | 0 | 3 | リスト (http://www.p-ban.com/implementation/chip.html)
例 | KOA | チップ抵抗 | RK73B2ATTD1002F | R1,R5,R9,R10 | 4 | 2 | 8 | 未実装 | SMD |  |  |  |  |  | 2012 |  | 4版 型式訂正、個数変更、 実装→未実装へ |  |  | 必要数 | 調達数 | 在庫状況 | メーカ | 調達品番 | 荷姿 | 納期 | 備考
1 □ | AKIZUKI | 2列ピンヘッダ | PH-2x04SG | CN8 | 1 | 8 | 8 | 実装 | DIP |  |  | 3 |  |  |  |  |  |  | □
2 □ | HIROSE | DF11コネクタ(PLUG) | DF11-4DP-2DSA(24) | CN5, CN9, CN15 | 3 | 4 | 12 | 実装 | DIP |  |  | 9 |  |  |  |  |  |  | □
3 □ | HIROSE | DF11コネクタ(PLUG) | DF11-14DP-2DSA(24) | CN7 | 1 | 14 | 14 | 実装 | DIP |  |  | 3 |  |  |  |  |  |  | □
4 □ | HIROSUGI | 取り付けスペーサ | VAB-3-10 | M2, M3 | 2 | 1 | 2 | 未実装 | DIP |  |  | 0 |  |  |  |  |  |  | □
5 □ | KOA | 金属皮膜抵抗 | MF1/4CC6800F | R59, R60 | 2 | 2 | 4 | 実装 | DIP |  |  | 6 |  |  |  |  |  |  | □
6 □ | NKK | トグルスイッチ | A-12AV | SW1, SW2, SW3 | 3 | 5 | 15 | 実装 | DIP |  |  | 9 |  |  |  |  |  |  | □
7 □ | TE | １列ピンヘッダ | 826646-4 | CN10 | 1 | 4 | 4 | 実装 | DIP |  |  | 3 |  |  |  |  |  |  | □
8 □ | TE | 基板実装BNCコネクタ | 5227161-3 | CN12, CN14 | 2 | 2 | 4 | 実装 | DIP |  |  | 6 |  |  |  |  |  |  | □
9 □ | TE | ポリスイッチ | RXEF050 | F2 | 1 | 2 | 2 | 実装 | DIP |  |  | 3 |  |  |  |  |  |  | □
10 □ | kingbright | インジケータ3mm | WP934EW/GD | D4 | 1 | 2 | 2 | 実装 | DIP |  |  | 3 |  |  |  |  |  |  | □
11 □ | kingbright | インジケータ3mm | WP934CB/ID | D5 | 1 | 2 | 2 | 実装 | DIP |  |  | 3 |  |  |  |  |  |  | □
12 □ |  |  |  |  |  |  |  |  |  |  |  |  |  |  |  |  |  |  | □
13 □ |  |  |  |  |  |  |  |  |  |  |  |  |  |  |  |  |  |  | □
14 □ |  |  |  |  |  |  |  |  |  |  |  |  |  |  |  |  |  |  | □
15 □ |  |  |  |  |  |  |  |  |  |  |  |  |  |  |  |  |  |  | □
16 □ |  |  |  |  |  |  |  |  |  |  |  |  |  |  |  |  |  |  | □
17 □ |  |  |  |  |  |  |  |  |  |  |  |  |  |  |  |  |  |  | □
18 □ |  |  |  |  |  |  |  |  |  |  |  |  |  |  |  |  |  |  | □
19 □ |  |  |  |  |  |  |  |  |  |  |  |  |  |  |  |  |  |  | □
20 □ |  |  |  |  |  |  |  |  |  |  |  |  |  |  |  |  |  |  | □
21 □ |  |  |  |  |  |  |  |  |  |  |  |  |  |  |  |  |  |  | □
22 □ |  |  |  |  |  |  |  |  |  |  |  |  |  |  |  |  |  |  | □
23 □ |  |  |  |  |  |  |  |  |  |  |  |  |  |  |  |  |  |  | □
24 □ |  |  |  |  |  |  |  |  |  |  |  |  |  |  |  |  |  |  | □
25 □ |  |  |  |  |  |  |  |  |  |  |  |  |  |  |  |  |  |  | □
26 □ |  |  |  |  |  |  |  |  |  |  |  |  |  |  |  |  |  |  | □
27 □ |  |  |  |  |  |  |  |  |  |  |  |  |  |  |  |  |  |  | □
28 □ |  |  |  |  |  |  |  |  |  |  |  |  |  |  |  |  |  |  | □
29 □ |  |  |  |  |  |  |  |  |  |  |  |  |  |  |  |  |  |  | □
30 □ |  |  |  |  |  |  |  |  |  |  |  |  |  |  |  |  |  |  | □
31 □ |  |  |  |  |  |  |  |  |  |  |  |  |  |  |  |  |  |  | □
32 □ |  |  |  |  |  |  |  |  |  |  |  |  |  |  |  |  |  |  | □
33 □ |  |  |  |  |  |  |  |  |  |  |  |  |  |  |  |  |  |  | □
34 □ |  |  |  |  |  |  |  |  |  |  |  |  |  |  |  |  |  |  | □
35 □ |  |  |  |  |  |  |  |  |  |  |  |  |  |  |  |  |  |  | □
36 □ |  |  |  |  |  |  |  |  |  |  |  |  |  |  |  |  |  |  | □
37 □ |  |  |  |  |  |  |  |  |  |  |  |  |  |  |  |  |  |  | □
38 □ |  |  |  |  |  |  |  |  |  |  |  |  |  |  |  |  |  |  | □
39 □ |  |  |  |  |  |  |  |  |  |  |  |  |  |  |  |  |  |  | □
40 □ |  |  |  |  |  |  |  |  |  |  |  |  |  |  |  |  |  |  | □
41 □ |  |  |  |  |  |  |  |  |  |  |  |  |  |  |  |  |  |  | □
42 □ |  |  |  |  |  |  |  |  |  |  |  |  |  |  |  |  |  |  | □
43 □ |  |  |  |  |  |  |  |  |  |  |  |  |  |  |  |  |  |  | □
44 □ |  |  |  |  |  |  |  |  |  |  |  |  |  |  |  |  |  |  | □
45 □ |  |  |  |  |  |  |  |  |  |  |  |  |  |  |  |  |  |  | □
46 □ |  |  |  |  |  |  |  |  |  |  |  |  |  |  |  |  |  |  | □
47 □ |  |  |  |  |  |  |  |  |  |  |  |  |  |  |  |  |  |  | □
48 □ |  |  |  |  |  |  |  |  |  |  |  |  |  |  |  |  |  |  | □
49 □ |  |  |  |  |  |  |  |  |  |  |  |  |  |  |  |  |  |  | □
50 □ |  |  |  |  |  |  |  |  |  |  |  |  |  |  |  |  |  |  | □
51 □ |  |  |  |  |  |  |  |  |  |  |  |  |  |  |  |  |  |  | □
52 □ |  |  |  |  |  |  |  |  |  |  |  |  |  |  |  |  |  |  | □
53 □ |  |  |  |  |  |  |  |  |  |  |  |  |  |  |  |  |  |  | □
54 □ |  |  |  |  |  |  |  |  |  |  |  |  |  |  |  |  |  |  | □
55 □ |  |  |  |  |  |  |  |  |  |  |  |  |  |  |  |  |  |  | □
56 □ |  |  |  |  |  |  |  |  |  |  |  |  |  |  |  |  |  |  | □
57 □ |  |  |  |  |  |  |  |  |  |  |  |  |  |  |  |  |  |  | □
58 □ |  |  |  |  |  |  |  |  |  |  |  |  |  |  |  |  |  |  | □
59 □ |  |  |  |  |  |  |  |  |  |  |  |  |  |  |  |  |  |  | □
60 □ |  |  |  |  |  |  |  |  |  |  |  |  |  |  |  |  |  |  | □
61 □ |  |  |  |  |  |  |  |  |  |  |  |  |  |  |  |  |  |  | □
62 □ |  |  |  |  |  |  |  |  |  |  |  |  |  |  |  |  |  |  | □
63 □ |  |  |  |  |  |  |  |  |  |  |  |  |  |  |  |  |  |  | □
64 □ |  |  |  |  |  |  |  |  |  |  |  |  |  |  |  |  |  |  | □
65 □ |  |  |  |  |  |  |  |  |  |  |  |  |  |  |  |  |  |  | □
66 □ |  |  |  |  |  |  |  |  |  |  |  |  |  |  |  |  |  |  | □
67 □ |  |  |  |  |  |  |  |  |  |  |  |  |  |  |  |  |  |  | □
68 □ |  |  |  |  |  |  |  |  |  |  |  |  |  |  |  |  |  |  | □
69 □ |  |  |  |  |  |  |  |  |  |  |  |  |  |  |  |  |  |  | □
70 □ |  |  |  |  |  |  |  |  |  |  |  |  |  |  |  |  |  |  | □
71 □ |  |  |  |  |  |  |  |  |  |  |  |  |  |  |  |  |  |  | □
72 □ |  |  |  |  |  |  |  |  |  |  |  |  |  |  |  |  |  |  | □
73 □ |  |  |  |  |  |  |  |  |  |  |  |  |  |  |  |  |  |  | □
74 □ |  |  |  |  |  |  |  |  |  |  |  |  |  |  |  |  |  |  | □
75 □ |  |  |  |  |  |  |  |  |  |  |  |  |  |  |  |  |  |  | □
76 □ |  |  |  |  |  |  |  |  |  |  |  |  |  |  |  |  |  |  | □
77 □ |  |  |  |  |  |  |  |  |  |  |  |  |  |  |  |  |  |  | □
78 □ |  |  |  |  |  |  |  |  |  |  |  |  |  |  |  |  |  |  | □
79 □ |  |  |  |  |  |  |  |  |  |  |  |  |  |  |  |  |  |  | □
80 □ |  |  |  |  |  |  |  |  |  |  |  |  |  |  |  |  |  |  | □
81 □ |  |  |  |  |  |  |  |  |  |  |  |  |  |  |  |  |  |  | □
82 □ |  |  |  |  |  |  |  |  |  |  |  |  |  |  |  |  |  |  | □
83 □ |  |  |  |  |  |  |  |  |  |  |  |  |  |  |  |  |  |  | □
84 □ |  |  |  |  |  |  |  |  |  |  |  |  |  |  |  |  |  |  | □
85 □ |  |  |  |  |  |  |  |  |  |  |  |  |  |  |  |  |  |  | □
86 □ |  |  |  |  |  |  |  |  |  |  |  |  |  |  |  |  |  |  | □
87 □ |  |  |  |  |  |  |  |  |  |  |  |  |  |  |  |  |  |  | □
88 □ |  |  |  |  |  |  |  |  |  |  |  |  |  |  |  |  |  |  | □
89 □ |  |  |  |  |  |  |  |  |  |  |  |  |  |  |  |  |  |  | □
90 □ |  |  |  |  |  |  |  |  |  |  |  |  |  |  |  |  |  |  | □
91 □ |  |  |  |  |  |  |  |  |  |  |  |  |  |  |  |  |  |  | □
92 □ |  |  |  |  |  |  |  |  |  |  |  |  |  |  |  |  |  |  | □
93 □ |  |  |  |  |  |  |  |  |  |  |  |  |  |  |  |  |  |  | □
94 □ |  |  |  |  |  |  |  |  |  |  |  |  |  |  |  |  |  |  | □
95 □ |  |  |  |  |  |  |  |  |  |  |  |  |  |  |  |  |  |  | □
96 □ |  |  |  |  |  |  |  |  |  |  |  |  |  |  |  |  |  |  | □
97 □ |  |  |  |  |  |  |  |  |  |  |  |  |  |  |  |  |  |  | □
98 □ |  |  |  |  |  |  |  |  |  |  |  |  |  |  |  |  |  |  | □
99 □ |  |  |  |  |  |  |  |  |  |  |  |  |  |  |  |  |  |  | □
100 □ |  |  |  |  |  |  |  |  |  |  |  |  |  |  |  |  |  |  | □
101 □ |  |  |  |  |  |  |  |  |  |  |  |  |  |  |  |  |  |  | □
102 □ |  |  |  |  |  |  |  |  |  |  |  |  |  |  |  |  |  |  | □
103 □ |  |  |  |  |  |  |  |  |  |  |  |  |  |  |  |  |  |  | □
104 □ |  |  |  |  |  |  |  |  |  |  |  |  |  |  |  |  |  |  | □
105 □ |  |  |  |  |  |  |  |  |  |  |  |  |  |  |  |  |  |  | □
106 □ |  |  |  |  |  |  |  |  |  |  |  |  |  |  |  |  |  |  | □
107 □ |  |  |  |  |  |  |  |  |  |  |  |  |  |  |  |  |  |  | □
108 □ |  |  |  |  |  |  |  |  |  |  |  |  |  |  |  |  |  |  | □
109 □ |  |  |  |  |  |  |  |  |  |  |  |  |  |  |  |  |  |  | □
110 □ |  |  |  |  |  |  |  |  |  |  |  |  |  |  |  |  |  |  | □
111 □ |  |  |  |  |  |  |  |  |  |  |  |  |  |  |  |  |  |  | □
112 □ |  |  |  |  |  |  |  |  |  |  |  |  |  |  |  |  |  |  | □
113 □ |  |  |  |  |  |  |  |  |  |  |  |  |  |  |  |  |  |  | □
114 □ |  |  |  |  |  |  |  |  |  |  |  |  |  |  |  |  |  |  | □
115 □ |  |  |  |  |  |  |  |  |  |  |  |  |  |  |  |  |  |  | □
116 □ |  |  |  |  |  |  |  |  |  |  |  |  |  |  |  |  |  |  | □
117 □ |  |  |  |  |  |  |  |  |  |  |  |  |  |  |  |  |  |  | □
118 □ |  |  |  |  |  |  |  |  |  |  |  |  |  |  |  |  |  |  | □
119 □ |  |  |  |  |  |  |  |  |  |  |  |  |  |  |  |  |  |  | □
120 □ |  |  |  |  |  |  |  |  |  |  |  |  |  |  |  |  |  |  | □
121 □ |  |  |  |  |  |  |  |  |  |  |  |  |  |  |  |  |  |  | □
122 □ |  |  |  |  |  |  |  |  |  |  |  |  |  |  |  |  |  |  | □
123 □ |  |  |  |  |  |  |  |  |  |  |  |  |  |  |  |  |  |  | □
124 □ |  |  |  |  |  |  |  |  |  |  |  |  |  |  |  |  |  |  | □
125 □ |  |  |  |  |  |  |  |  |  |  |  |  |  |  |  |  |  |  | □
126 □ |  |  |  |  |  |  |  |  |  |  |  |  |  |  |  |  |  |  | □
127 □ |  |  |  |  |  |  |  |  |  |  |  |  |  |  |  |  |  |  | □
128 □ |  |  |  |  |  |  |  |  |  |  |  |  |  |  |  |  |  |  | □
129 □ |  |  |  |  |  |  |  |  |  |  |  |  |  |  |  |  |  |  | □
130 □ |  |  |  |  |  |  |  |  |  |  |  |  |  |  |  |  |  |  | □
131 □ |  |  |  |  |  |  |  |  |  |  |  |  |  |  |  |  |  |  | □
132 □ |  |  |  |  |  |  |  |  |  |  |  |  |  |  |  |  |  |  | □
133 □ |  |  |  |  |  |  |  |  |  |  |  |  |  |  |  |  |  |  | □
134 □ |  |  |  |  |  |  |  |  |  |  |  |  |  |  |  |  |  |  | □
135 □ |  |  |  |  |  |  |  |  |  |  |  |  |  |  |  |  |  |  | □
136 □ |  |  |  |  |  |  |  |  |  |  |  |  |  |  |  |  |  |  | □
137 □ |  |  |  |  |  |  |  |  |  |  |  |  |  |  |  |  |  |  | □
138 □ |  |  |  |  |  |  |  |  |  |  |  |  |  |  |  |  |  |  | □
139 □ |  |  |  |  |  |  |  |  |  |  |  |  |  |  |  |  |  |  | □
140 □ |  |  |  |  |  |  |  |  |  |  |  |  |  |  |  |  |  |  | □
141 □ |  |  |  |  |  |  |  |  |  |  |  |  |  |  |  |  |  |  | □
142 □ |  |  |  |  |  |  |  |  |  |  |  |  |  |  |  |  |  |  | □
143 □ |  |  |  |  |  |  |  |  |  |  |  |  |  |  |  |  |  |  | □
144 □ |  |  |  |  |  |  |  |  |  |  |  |  |  |  |  |  |  |  | □
145 □ |  |  |  |  |  |  |  |  |  |  |  |  |  |  |  |  |  |  | □
146 □ |  |  |  |  |  |  |  |  |  |  |  |  |  |  |  |  |  |  | □
147 □ |  |  |  |  |  |  |  |  |  |  |  |  |  |  |  |  |  |  | □
148 □ |  |  |  |  |  |  |  |  |  |  |  |  |  |  |  |  |  |  | □

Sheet: 無償提供部品一覧
このシートの内容は変更しないでください。
メーカー型番 |  | メーカー | サイズ | 定数 | 許容差 | 定格
RK73Z1ETTP | ○ | KOA | 1005 | 0 | － | 1A
RK73H1ETTP1R00F | ○ | KOA | 1005 | 1 | ±1% | 0.1W
RK73B1ETTP1R0J | ○ | KOA | 1005 | 1 | ±5% | 0.1W
RK73H1ETTP1R10F | ○ | KOA | 1005 | 1.1 | ±1% | 0.1W
RK73B1ETTP1R1J | ○ | KOA | 1005 | 1.1 | ±5% | 0.1W
RK73H1ETTP1R20F | ○ | KOA | 1005 | 1.2 | ±1% | 0.1W
RK73B1ETTP1R2J | ○ | KOA | 1005 | 1.2 | ±5% | 0.1W
RK73H1ETTP1R30F | ○ | KOA | 1005 | 1.3 | ±1% | 0.1W
RK73B1ETTP1R3J | ○ | KOA | 1005 | 1.3 | ±5% | 0.1W
RK73H1ETTP1R50F | ○ | KOA | 1005 | 1.5 | ±1% | 0.1W
RK73B1ETTP1R5J | ○ | KOA | 1005 | 1.5 | ±5% | 0.1W
RK73H1ETTP1R60F | ○ | KOA | 1005 | 1.6 | ±1% | 0.1W
RK73B1ETTP1R6J | ○ | KOA | 1005 | 1.6 | ±5% | 0.1W
RK73H1ETTP1R80F | ○ | KOA | 1005 | 1.8 | ±1% | 0.1W
RK73B1ETTP1R8J | ○ | KOA | 1005 | 1.8 | ±5% | 0.1W
RK73H1ETTP2R00F | ○ | KOA | 1005 | 2 | ±1% | 0.1W
RK73B1ETTP2R0J | ○ | KOA | 1005 | 2 | ±5% | 0.1W
RK73H1ETTP2R20F | ○ | KOA | 1005 | 2.2 | ±1% | 0.1W
RK73B1ETTP2R2J | ○ | KOA | 1005 | 2.2 | ±5% | 0.1W
RK73H1ETTP2R40F | ○ | KOA | 1005 | 2.4 | ±1% | 0.1W
RK73B1ETTP2R4J | ○ | KOA | 1005 | 2.4 | ±5% | 0.1W
RK73H1ETTP2R70F | ○ | KOA | 1005 | 2.7 | ±1% | 0.1W
RK73B1ETTP2R7J | ○ | KOA | 1005 | 2.7 | ±5% | 0.1W
RK73H1ETTP3R00F | ○ | KOA | 1005 | 3 | ±1% | 0.1W
RK73B1ETTP3R0J | ○ | KOA | 1005 | 3 | ±5% | 0.1W
RK73H1ETTP3R30F | ○ | KOA | 1005 | 3.3 | ±1% | 0.1W
RK73B1ETTP3R3J | ○ | KOA | 1005 | 3.3 | ±5% | 0.1W
RK73H1ETTP3R60F | ○ | KOA | 1005 | 3.6 | ±1% | 0.1W
RK73B1ETTP3R6J | ○ | KOA | 1005 | 3.6 | ±5% | 0.1W
RK73H1ETTP3R90F | ○ | KOA | 1005 | 3.9 | ±1% | 0.1W
RK73B1ETTP3R9J | ○ | KOA | 1005 | 3.9 | ±5% | 0.1W
RK73H1ETTP4R30F | ○ | KOA | 1005 | 4.3 | ±1% | 0.1W
RK73B1ETTP4R3J | ○ | KOA | 1005 | 4.3 | ±5% | 0.1W
RK73H1ETTP4R70F | ○ | KOA | 1005 | 4.7 | ±1% | 0.1W
RK73B1ETTP4R7J | ○ | KOA | 1005 | 4.7 | ±5% | 0.1W
RK73H1ETTP5R10F | ○ | KOA | 1005 | 5.1 | ±1% | 0.1W
RK73B1ETTP5R1J | ○ | KOA | 1005 | 5.1 | ±5% | 0.1W
RK73H1ETTP5R60F | ○ | KOA | 1005 | 5.6 | ±1% | 0.1W
RK73B1ETTP5R6J | ○ | KOA | 1005 | 5.6 | ±5% | 0.1W
RK73H1ETTP6R20F | ○ | KOA | 1005 | 6.2 | ±1% | 0.1W
RK73B1ETTP6R2J | ○ | KOA | 1005 | 6.2 | ±5% | 0.1W
RK73H1ETTP6R80F | ○ | KOA | 1005 | 6.8 | ±1% | 0.1W
RK73B1ETTP6R8J | ○ | KOA | 1005 | 6.8 | ±5% | 0.1W
RK73H1ETTP7R50F | ○ | KOA | 1005 | 7.5 | ±1% | 0.1W
RK73B1ETTP7R5J | ○ | KOA | 1005 | 7.5 | ±5% | 0.1W
RK73H1ETTP8R20F | ○ | KOA | 1005 | 8.2 | ±1% | 0.1W
RK73B1ETTP8R2J | ○ | KOA | 1005 | 8.2 | ±5% | 0.1W
RK73H1ETTP9R10F | ○ | KOA | 1005 | 9.1 | ±1% | 0.1W
RK73B1ETTP9R1J | ○ | KOA | 1005 | 9.1 | ±5% | 0.1W
RK73H1ETTP10R0F | ○ | KOA | 1005 | 10 | ±1% | 0.1W
RK73B1ETTP100J | ○ | KOA | 1005 | 10 | ±5% | 0.1W
RK73H1ETTP11R0F | ○ | KOA | 1005 | 11 | ±1% | 0.1W
RK73B1ETTP110J | ○ | KOA | 1005 | 11 | ±5% | 0.1W
RK73H1ETTP12R0F | ○ | KOA | 1005 | 12 | ±1% | 0.1W
RK73B1ETTP120J | ○ | KOA | 1005 | 12 | ±5% | 0.1W
RK73H1ETTP13R0F | ○ | KOA | 1005 | 13 | ±1% | 0.1W
RK73B1ETTP130J | ○ | KOA | 1005 | 13 | ±5% | 0.1W
RK73H1ETTP15R0F | ○ | KOA | 1005 | 15 | ±1% | 0.1W
RK73B1ETTP150J | ○ | KOA | 1005 | 15 | ±5% | 0.1W
RK73H1ETTP16R0F | ○ | KOA | 1005 | 16 | ±1% | 0.1W
RK73B1ETTP160J | ○ | KOA | 1005 | 16 | ±5% | 0.1W
RK73H1ETTP18R0F | ○ | KOA | 1005 | 18 | ±1% | 0.1W
RK73B1ETTP180J | ○ | KOA | 1005 | 18 | ±5% | 0.1W
RK73H1ETTP20R0F | ○ | KOA | 1005 | 20 | ±1% | 0.1W
RK73B1ETTP200J | ○ | KOA | 1005 | 20 | ±5% | 0.1W
RK73H1ETTP22R0F | ○ | KOA | 1005 | 22 | ±1% | 0.1W
RK73B1ETTP220J | ○ | KOA | 1005 | 22 | ±5% | 0.1W
RK73H1ETTP24R0F | ○ | KOA | 1005 | 24 | ±1% | 0.1W
RK73B1ETTP240J | ○ | KOA | 1005 | 24 | ±5% | 0.1W
RK73H1ETTP27R0F | ○ | KOA | 1005 | 27 | ±1% | 0.1W
RK73B1ETTP270J | ○ | KOA | 1005 | 27 | ±5% | 0.1W
RK73H1ETTP30R0F | ○ | KOA | 1005 | 30 | ±1% | 0.1W
RK73B1ETTP300J | ○ | KOA | 1005 | 30 | ±5% | 0.1W
RK73H1ETTP33R0F | ○ | KOA | 1005 | 33 | ±1% | 0.1W
RK73B1ETTP330J | ○ | KOA | 1005 | 33 | ±5% | 0.1W
RK73H1ETTP36R0F | ○ | KOA | 1005 | 36 | ±1% | 0.1W
RK73B1ETTP360J | ○ | KOA | 1005 | 36 | ±5% | 0.1W
RK73H1ETTP39R0F | ○ | KOA | 1005 | 39 | ±1% | 0.1W
RK73B1ETTP390J | ○ | KOA | 1005 | 39 | ±5% | 0.1W
RK73H1ETTP43R0F | ○ | KOA | 1005 | 43 | ±1% | 0.1W
RK73B1ETTP430J | ○ | KOA | 1005 | 43 | ±5% | 0.1W
RK73H1ETTP47R0F | ○ | KOA | 1005 | 47 | ±1% | 0.1W
RK73B1ETTP470J | ○ | KOA | 1005 | 47 | ±5% | 0.1W
RK73H1ETTP51R0F | ○ | KOA | 1005 | 51 | ±1% | 0.1W
RK73B1ETTP510J | ○ | KOA | 1005 | 51 | ±5% | 0.1W
RK73H1ETTP56R0F | ○ | KOA | 1005 | 56 | ±1% | 0.1W
RK73B1ETTP560J | ○ | KOA | 1005 | 56 | ±5% | 0.1W
RK73H1ETTP62R0F | ○ | KOA | 1005 | 62 | ±1% | 0.1W
RK73B1ETTP620J | ○ | KOA | 1005 | 62 | ±5% | 0.1W
RK73H1ETTP68R0F | ○ | KOA | 1005 | 68 | ±1% | 0.1W
RK73B1ETTP680J | ○ | KOA | 1005 | 68 | ±5% | 0.1W
RK73H1ETTP75R0F | ○ | KOA | 1005 | 75 | ±1% | 0.1W
RK73B1ETTP750J | ○ | KOA | 1005 | 75 | ±5% | 0.1W
RK73H1ETTP82R0F | ○ | KOA | 1005 | 82 | ±1% | 0.1W
RK73B1ETTP820J | ○ | KOA | 1005 | 82 | ±5% | 0.1W
RK73H1ETTP91R0F | ○ | KOA | 1005 | 91 | ±1% | 0.1W
RK73B1ETTP910J | ○ | KOA | 1005 | 91 | ±5% | 0.1W
RK73H1ETTP1000F | ○ | KOA | 1005 | 100 | ±1% | 0.1W
RK73B1ETTP101J | ○ | KOA | 1005 | 100 | ±5% | 0.1W
RK73H1ETTP1100F | ○ | KOA | 1005 | 110 | ±1% | 0.1W
RK73B1ETTP111J | ○ | KOA | 1005 | 110 | ±5% | 0.1W
RK73H1ETTP1200F | ○ | KOA | 1005 | 120 | ±1% | 0.1W
RK73B1ETTP121J | ○ | KOA | 1005 | 120 | ±5% | 0.1W
RK73H1ETTP1300F | ○ | KOA | 1005 | 130 | ±1% | 0.1W
RK73B1ETTP131J | ○ | KOA | 1005 | 130 | ±5% | 0.1W
RK73H1ETTP1500F | ○ | KOA | 1005 | 150 | ±1% | 0.1W
RK73B1ETTP151J | ○ | KOA | 1005 | 150 | ±5% | 0.1W
RK73H1ETTP1600F | ○ | KOA | 1005 | 160 | ±1% | 0.1W
RK73B1ETTP161J | ○ | KOA | 1005 | 160 | ±5% | 0.1W
RK73H1ETTP1800F | ○ | KOA | 1005 | 180 | ±1% | 0.1W
RK73B1ETTP181J | ○ | KOA | 1005 | 180 | ±5% | 0.1W
RK73H1ETTP2000F | ○ | KOA | 1005 | 200 | ±1% | 0.1W
RK73B1ETTP201J | ○ | KOA | 1005 | 200 | ±5% | 0.1W
RK73H1ETTP2200F | ○ | KOA | 1005 | 220 | ±1% | 0.1W
RK73B1ETTP221J | ○ | KOA | 1005 | 220 | ±5% | 0.1W
RK73H1ETTP2400F | ○ | KOA | 1005 | 240 | ±1% | 0.1W
RK73B1ETTP241J | ○ | KOA | 1005 | 240 | ±5% | 0.1W
RK73H1ETTP2700F | ○ | KOA | 1005 | 270 | ±1% | 0.1W
RK73B1ETTP271J | ○ | KOA | 1005 | 270 | ±5% | 0.1W
RK73H1ETTP3000F | ○ | KOA | 1005 | 300 | ±1% | 0.1W
RK73B1ETTP301J | ○ | KOA | 1005 | 300 | ±5% | 0.1W
RK73H1ETTP3300F | ○ | KOA | 1005 | 330 | ±1% | 0.1W
RK73B1ETTP331J | ○ | KOA | 1005 | 330 | ±5% | 0.1W
RK73H1ETTP3600F | ○ | KOA | 1005 | 360 | ±1% | 0.1W
RK73B1ETTP361J | ○ | KOA | 1005 | 360 | ±5% | 0.1W
RK73H1ETTP3900F | ○ | KOA | 1005 | 390 | ±1% | 0.1W
RK73B1ETTP391J | ○ | KOA | 1005 | 390 | ±5% | 0.1W
RK73H1ETTP4300F | ○ | KOA | 1005 | 430 | ±1% | 0.1W
RK73B1ETTP431J | ○ | KOA | 1005 | 430 | ±5% | 0.1W
RK73H1ETTP4700F | ○ | KOA | 1005 | 470 | ±1% | 0.1W
RK73B1ETTP471J | ○ | KOA | 1005 | 470 | ±5% | 0.1W
RK73H1ETTP5100F | ○ | KOA | 1005 | 510 | ±1% | 0.1W
RK73B1ETTP511J | ○ | KOA | 1005 | 510 | ±5% | 0.1W
RK73H1ETTP5600F | ○ | KOA | 1005 | 560 | ±1% | 0.1W
RK73B1ETTP561J | ○ | KOA | 1005 | 560 | ±5% | 0.1W
RK73H1ETTP6200F | ○ | KOA | 1005 | 620 | ±1% | 0.1W
RK73B1ETTP621J | ○ | KOA | 1005 | 620 | ±5% | 0.1W
RK73H1ETTP6800F | ○ | KOA | 1005 | 680 | ±1% | 0.1W
RK73B1ETTP681J | ○ | KOA | 1005 | 680 | ±5% | 0.1W
RK73H1ETTP7500F | ○ | KOA | 1005 | 750 | ±1% | 0.1W
RK73B1ETTP751J | ○ | KOA | 1005 | 750 | ±5% | 0.1W
RK73H1ETTP8200F | ○ | KOA | 1005 | 820 | ±1% | 0.1W
RK73B1ETTP821J | ○ | KOA | 1005 | 820 | ±5% | 0.1W
RK73H1ETTP9100F | ○ | KOA | 1005 | 910 | ±1% | 0.1W
RK73B1ETTP911J | ○ | KOA | 1005 | 910 | ±5% | 0.1W
RK73H1ETTP1001F | ○ | KOA | 1005 | 1.00k | ±1% | 0.1W
RK73B1ETTP102J | ○ | KOA | 1005 | 1k | ±5% | 0.1W
RK73H1ETTP1101F | ○ | KOA | 1005 | 1.10k | ±1% | 0.1W
RK73B1ETTP112J | ○ | KOA | 1005 | 1.1k | ±5% | 0.1W
RK73H1ETTP1201F | ○ | KOA | 1005 | 1.20k | ±1% | 0.1W
RK73B1ETTP122J | ○ | KOA | 1005 | 1.2k | ±5% | 0.1W
RK73H1ETTP1301F | ○ | KOA | 1005 | 1.30k | ±1% | 0.1W
RK73B1ETTP132J | ○ | KOA | 1005 | 1.3k | ±5% | 0.1W
RK73H1ETTP1501F | ○ | KOA | 1005 | 1.50k | ±1% | 0.1W
RK73B1ETTP152J | ○ | KOA | 1005 | 1.5k | ±5% | 0.1W
RK73H1ETTP1601F | ○ | KOA | 1005 | 1.60k | ±1% | 0.1W
RK73B1ETTP162J | ○ | KOA | 1005 | 1.6k | ±5% | 0.1W
RK73H1ETTP1801F | ○ | KOA | 1005 | 1.80k | ±1% | 0.1W
RK73B1ETTP182J | ○ | KOA | 1005 | 1.8k | ±5% | 0.1W
RK73H1ETTP2001F | ○ | KOA | 1005 | 2.00k | ±1% | 0.1W
RK73B1ETTP202J | ○ | KOA | 1005 | 2.0k | ±5% | 0.1W
RK73H1ETTP2201F | ○ | KOA | 1005 | 2.20k | ±1% | 0.1W
RK73B1ETTP222J | ○ | KOA | 1005 | 2.2k | ±5% | 0.1W
RK73H1ETTP2401F | ○ | KOA | 1005 | 2.40k | ±1% | 0.1W
RK73B1ETTP242J | ○ | KOA | 1005 | 2.4k | ±5% | 0.1W
RK73H1ETTP2701F | ○ | KOA | 1005 | 2.70k | ±1% | 0.1W
RK73B1ETTP272J | ○ | KOA | 1005 | 2.7k | ±5% | 0.1W
RK73H1ETTP3001F | ○ | KOA | 1005 | 3.00k | ±1% | 0.1W
RK73B1ETTP302J | ○ | KOA | 1005 | 3.0k | ±5% | 0.1W
RK73H1ETTP3301F | ○ | KOA | 1005 | 3.30k | ±1% | 0.1W
RK73B1ETTP332J | ○ | KOA | 1005 | 3.3k | ±5% | 0.1W
RK73H1ETTP3601F | ○ | KOA | 1005 | 3.60k | ±1% | 0.1W
RK73B1ETTP362J | ○ | KOA | 1005 | 3.6k | ±5% | 0.1W
RK73H1ETTP3901F | ○ | KOA | 1005 | 3.90k | ±1% | 0.1W
RK73B1ETTP392J | ○ | KOA | 1005 | 3.9k | ±5% | 0.1W
RK73H1ETTP4301F | ○ | KOA | 1005 | 4.30k | ±1% | 0.1W
RK73B1ETTP432J | ○ | KOA | 1005 | 4.3k | ±5% | 0.1W
RK73H1ETTP4701F | ○ | KOA | 1005 | 4.70k | ±1% | 0.1W
RK73B1ETTP472J | ○ | KOA | 1005 | 4.7k | ±5% | 0.1W
RK73H1ETTP5101F | ○ | KOA | 1005 | 5.10k | ±1% | 0.1W
RK73B1ETTP512J | ○ | KOA | 1005 | 5.1k | ±5% | 0.1W
RK73H1ETTP5601F | ○ | KOA | 1005 | 5.60k | ±1% | 0.1W
RK73B1ETTP562J | ○ | KOA | 1005 | 5.6k | ±5% | 0.1W
RK73H1ETTP6201F | ○ | KOA | 1005 | 6.20k | ±1% | 0.1W
RK73B1ETTP622J | ○ | KOA | 1005 | 6.2k | ±5% | 0.1W
RK73H1ETTP6801F | ○ | KOA | 1005 | 6.80k | ±1% | 0.1W
RK73B1ETTP682J | ○ | KOA | 1005 | 6.8k | ±5% | 0.1W
RK73H1ETTP7501F | ○ | KOA | 1005 | 7.50k | ±1% | 0.1W
RK73B1ETTP752J | ○ | KOA | 1005 | 7.5k | ±5% | 0.1W
RK73H1ETTP8201F | ○ | KOA | 1005 | 8.20k | ±1% | 0.1W
RK73B1ETTP822J | ○ | KOA | 1005 | 8.2k | ±5% | 0.1W
RK73H1ETTP9101F | ○ | KOA | 1005 | 9.10k | ±1% | 0.1W
RK73B1ETTP912J | ○ | KOA | 1005 | 9.1k | ±5% | 0.1W
RK73H1ETTP1002F | ○ | KOA | 1005 | 10.0k | ±1% | 0.1W
RK73B1ETTP103J | ○ | KOA | 1005 | 10k | ±5% | 0.1W
RK73H1ETTP1102F | ○ | KOA | 1005 | 11.0k | ±1% | 0.1W
RK73B1ETTP113J | ○ | KOA | 1005 | 11k | ±5% | 0.1W
RK73H1ETTP1202F | ○ | KOA | 1005 | 12.0k | ±1% | 0.1W
RK73B1ETTP123J | ○ | KOA | 1005 | 12k | ±5% | 0.1W
RK73H1ETTP1302F | ○ | KOA | 1005 | 13.0k | ±1% | 0.1W
RK73B1ETTP133J | ○ | KOA | 1005 | 13k | ±5% | 0.1W
RK73H1ETTP1502F | ○ | KOA | 1005 | 15.0k | ±1% | 0.1W
RK73B1ETTP153J | ○ | KOA | 1005 | 15k | ±5% | 0.1W
RK73H1ETTP1602F | ○ | KOA | 1005 | 16.0k | ±1% | 0.1W
RK73B1ETTP163J | ○ | KOA | 1005 | 16k | ±5% | 0.1W
RK73H1ETTP1802F | ○ | KOA | 1005 | 18.0k | ±1% | 0.1W
RK73B1ETTP183J | ○ | KOA | 1005 | 18k | ±5% | 0.1W
RK73H1ETTP2002F | ○ | KOA | 1005 | 20.0k | ±1% | 0.1W
RK73B1ETTP203J | ○ | KOA | 1005 | 20k | ±5% | 0.1W
RK73H1ETTP2202F | ○ | KOA | 1005 | 22.0k | ±1% | 0.1W
RK73B1ETTP223J | ○ | KOA | 1005 | 22k | ±5% | 0.1W
RK73H1ETTP2402F | ○ | KOA | 1005 | 24.0k | ±1% | 0.1W
RK73B1ETTP243J | ○ | KOA | 1005 | 24k | ±5% | 0.1W
RK73H1ETTP2702F | ○ | KOA | 1005 | 27.0k | ±1% | 0.1W
RK73B1ETTP273J | ○ | KOA | 1005 | 27k | ±5% | 0.1W
RK73H1ETTP3002F | ○ | KOA | 1005 | 30.0k | ±1% | 0.1W
RK73B1ETTP303J | ○ | KOA | 1005 | 30k | ±5% | 0.1W
RK73H1ETTP3302F | ○ | KOA | 1005 | 33.0k | ±1% | 0.1W
RK73B1ETTP333J | ○ | KOA | 1005 | 33k | ±5% | 0.1W
RK73H1ETTP3602F | ○ | KOA | 1005 | 36.0k | ±1% | 0.1W
RK73B1ETTP363J | ○ | KOA | 1005 | 36k | ±5% | 0.1W
RK73H1ETTP3902F | ○ | KOA | 1005 | 39.0k | ±1% | 0.1W
RK73B1ETTP393J | ○ | KOA | 1005 | 39k | ±5% | 0.1W
RK73H1ETTP4302F | ○ | KOA | 1005 | 43.0k | ±1% | 0.1W
RK73B1ETTP433J | ○ | KOA | 1005 | 43k | ±5% | 0.1W
RK73H1ETTP4702F | ○ | KOA | 1005 | 47.0k | ±1% | 0.1W
RK73B1ETTP473J | ○ | KOA | 1005 | 47k | ±5% | 0.1W
RK73H1ETTP5102F | ○ | KOA | 1005 | 51.0k | ±1% | 0.1W
RK73B1ETTP513J | ○ | KOA | 1005 | 51k | ±5% | 0.1W
RK73H1ETTP5602F | ○ | KOA | 1005 | 56.0k | ±1% | 0.1W
RK73B1ETTP563J | ○ | KOA | 1005 | 56k | ±5% | 0.1W
RK73H1ETTP6202F | ○ | KOA | 1005 | 62.0k | ±1% | 0.1W
RK73B1ETTP623J | ○ | KOA | 1005 | 62k | ±5% | 0.1W
RK73H1ETTP6802F | ○ | KOA | 1005 | 68.0k | ±1% | 0.1W
RK73B1ETTP683J | ○ | KOA | 1005 | 68k | ±5% | 0.1W
RK73H1ETTP7502F | ○ | KOA | 1005 | 75.0k | ±1% | 0.1W
RK73B1ETTP753J | ○ | KOA | 1005 | 75k | ±5% | 0.1W
RK73H1ETTP8202F | ○ | KOA | 1005 | 82.0k | ±1% | 0.1W
RK73B1ETTP823J | ○ | KOA | 1005 | 82k | ±5% | 0.1W
RK73H1ETTP9102F | ○ | KOA | 1005 | 91.0k | ±1% | 0.1W
RK73B1ETTP913J | ○ | KOA | 1005 | 91k | ±5% | 0.1W
RK73H1ETTP1003F | ○ | KOA | 1005 | 100k | ±1% | 0.1W
RK73B1ETTP104J | ○ | KOA | 1005 | 100k | ±5% | 0.1W
RK73H1ETTP1103F | ○ | KOA | 1005 | 110k | ±1% | 0.1W
RK73B1ETTP114J | ○ | KOA | 1005 | 110k | ±5% | 0.1W
RK73H1ETTP1203F | ○ | KOA | 1005 | 120k | ±1% | 0.1W
RK73B1ETTP124J | ○ | KOA | 1005 | 120k | ±5% | 0.1W
RK73H1ETTP1303F | ○ | KOA | 1005 | 130k | ±1% | 0.1W
RK73B1ETTP134J | ○ | KOA | 1005 | 130k | ±5% | 0.1W
RK73H1ETTP1503F | ○ | KOA | 1005 | 150k | ±1% | 0.1W
RK73B1ETTP154J | ○ | KOA | 1005 | 150k | ±5% | 0.1W
RK73H1ETTP1603F | ○ | KOA | 1005 | 160k | ±1% | 0.1W
RK73B1ETTP164J | ○ | KOA | 1005 | 160k | ±5% | 0.1W
RK73H1ETTP1803F | ○ | KOA | 1005 | 180k | ±1% | 0.1W
RK73B1ETTP184J | ○ | KOA | 1005 | 180k | ±5% | 0.1W
RK73H1ETTP2003F | ○ | KOA | 1005 | 200k | ±1% | 0.1W
RK73B1ETTP204J | ○ | KOA | 1005 | 200k | ±5% | 0.1W
RK73H1ETTP2203F | ○ | KOA | 1005 | 220k | ±1% | 0.1W
RK73B1ETTP224J | ○ | KOA | 1005 | 220k | ±5% | 0.1W
RK73H1ETTP2403F | ○ | KOA | 1005 | 240k | ±1% | 0.1W
RK73B1ETTP244J | ○ | KOA | 1005 | 240k | ±5% | 0.1W
RK73H1ETTP2703F | ○ | KOA | 1005 | 270k | ±1% | 0.1W
RK73B1ETTP274J | ○ | KOA | 1005 | 270k | ±5% | 0.1W
RK73H1ETTP3003F | ○ | KOA | 1005 | 300k | ±1% | 0.1W
RK73B1ETTP304J | ○ | KOA | 1005 | 300k | ±5% | 0.1W
RK73H1ETTP3303F | ○ | KOA | 1005 | 330k | ±1% | 0.1W
RK73B1ETTP334J | ○ | KOA | 1005 | 330k | ±5% | 0.1W
RK73H1ETTP3603F | ○ | KOA | 1005 | 360k | ±1% | 0.1W
RK73B1ETTP364J | ○ | KOA | 1005 | 360k | ±5% | 0.1W
RK73H1ETTP3903F | ○ | KOA | 1005 | 390k | ±1% | 0.1W
RK73B1ETTP394J | ○ | KOA | 1005 | 390k | ±5% | 0.1W
RK73H1ETTP4303F | ○ | KOA | 1005 | 430k | ±1% | 0.1W
RK73B1ETTP434J | ○ | KOA | 1005 | 430k | ±5% | 0.1W
RK73H1ETTP4703F | ○ | KOA | 1005 | 470k | ±1% | 0.1W
RK73B1ETTP474J | ○ | KOA | 1005 | 470k | ±5% | 0.1W
RK73H1ETTP5103F | ○ | KOA | 1005 | 510k | ±1% | 0.1W
RK73B1ETTP514J | ○ | KOA | 1005 | 510k | ±5% | 0.1W
RK73H1ETTP5603F | ○ | KOA | 1005 | 560k | ±1% | 0.1W
RK73B1ETTP564J | ○ | KOA | 1005 | 560k | ±5% | 0.1W
RK73H1ETTP6203F | ○ | KOA | 1005 | 620k | ±1% | 0.1W
RK73B1ETTP624J | ○ | KOA | 1005 | 620k | ±5% | 0.1W
RK73H1ETTP6803F | ○ | KOA | 1005 | 680k | ±1% | 0.1W
RK73B1ETTP684J | ○ | KOA | 1005 | 680k | ±5% | 0.1W
RK73H1ETTP7503F | ○ | KOA | 1005 | 750k | ±1% | 0.1W
RK73B1ETTP754J | ○ | KOA | 1005 | 750k | ±5% | 0.1W
RK73H1ETTP8203F | ○ | KOA | 1005 | 820k | ±1% | 0.1W
RK73B1ETTP824J | ○ | KOA | 1005 | 820k | ±5% | 0.1W
RK73H1ETTP9103F | ○ | KOA | 1005 | 910k | ±1% | 0.1W
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

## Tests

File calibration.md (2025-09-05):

# モニタ出力の値づけ（キャリブレーション）
このノートでは、コイルドライバの電流モニタ出力の電圧値とコイルを流れる電流値の係数（電流電圧変換係数）を実測値から値づけする手順例を示します。  
この作業はコイルに流れる実際の電流値を電流モニタ出力の電圧から把握するために不可欠です。  
この手順は実際に機器を製造するときに用いた方法ですが、他の方法でも値づけは可能だと思いますので参考までにご覧ください。</br>

## 修正履歴
- 初版：2025/07/25  宮本政和
---
# 概要
- キャリブレーション時の機器の接続

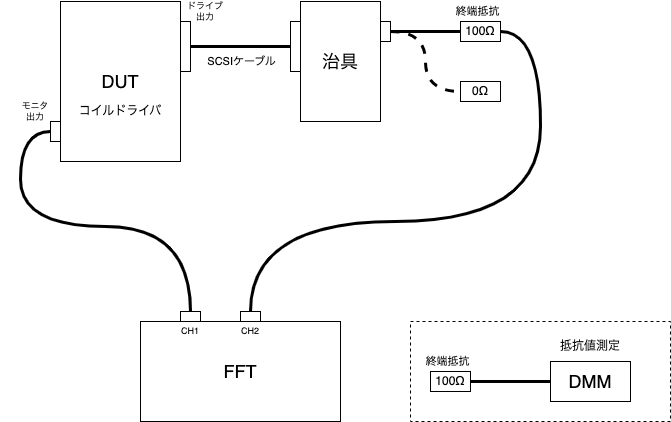
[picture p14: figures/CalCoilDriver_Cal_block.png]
Block Diagram for calibration

<!-- 図の編集は：https://app.diagrams.net/ にて figures/CalCoilDriver_Cal_block.drawio を開いてください-->

## キャリブレーションの目的

本装置は接続されたコイルを一定の電流で駆動し、その電流値は電流モニタ出力から電圧として観測できる様になっています。このモニタ出力の電圧値は設計された電流電圧変換係数に従いコイルに流れる電流に比例した電圧を発生しますが、部品のばらつき等によるエラーを含んでいます。このエラーを把握し、電流モニタ出力電圧から信頼性の高い電流値を推測するために電流電圧変換係数の値づけ(キャリブレーション)を行います。

値づけのためには、実際にコイルに流れる電流とコイルドライバのモニタ出力の電圧を同時に観測する必要があります。  

この値づけ作業の結果、算出されるのは以下のパラメタです。
- 電流モニタ出力の電流ー電圧変換係数 

## 値づけのための計測
値づけのための計測の概要は以下の通りです。

1. **コイルに流れる電流を直接計測する**  
  本来はコイルに流れている電流を電流計のような測定器で直接計測するのがベターだと思いますが、ここではコイルの代わりに終端抵抗を駆動し、その両端に発生する電圧を測定することで流れている電流を推測します。  
  直流抵抗がほぼゼロのコイルを駆動した時と比較して、発生した電圧の分だけ駆動電流の絶対値は低くなります。しかし、変換係数の値づけに電流の絶対値は関係しないため問題ないと判断しています。（リニアリティは回路・部品で担保されていると想定しています）  
  コイルを駆動した時の電流値については、変換係数の算出後に終端抵抗を0Ωにして確認します。  
  
1. **同時に電流モニタ出力の電圧値を計測する**  
上記の終端抵抗に発生する電圧の計測と同時に、装置の電流モニタ出力の電圧計測します。  
これにより、「同じ電流を2つの方法で測定した結果」を得ることができます。

1. **同時に電流モニタ出力の電圧値を計測する**  
終端抵抗の電圧計測を基準として電流モニタ出力の電圧を値づけする計算を行います。  

# 必要機器
- **DMM(抵抗測定)**  
  終端抵抗の値を計測します。確度高く計測するために４端子法での計測をお勧めします。
- **信号モニタ用ジグ**  
  コイルドライバの出力(SCSIコネクタ)をBNCに変換するためのジグです。コイルドライブ出力に終端抵抗を接続するために使用します。</br>
- **SCSIケーブル**  
  信号モニタ用ジグと機器を繋ぐケーブルです</br>
- **終端抵抗(100Ω/0Ω)**  
    ドライブされるコイルのダミーとして使います。100Ωの両端の電圧を計測することで、実際にコイルに流れる電流を算出します。  
    0Ωの終端抵抗は、モニタ出力の値づけ後にコイルに流れる電流値を確認するために使用します。</br>
- **FFTアナライザ**  
  コイルドライバのモニタ出力端子と終端抵抗の交流電圧を計測します。非常に小さい電圧（1mVrms程度）を計測するので、ノイズを含めて計測してしまう交流電圧計は使用できません。  
  ロックインアンプでも計測可能だと思います。  
  モニタ出力の電圧値とコイルに流れる電流（終端抵抗の両端の電圧）を同時に計測する必要があるため、2ch同時計測できる計測器が望ましいです。また、測定器の入力は測定器のGNDからフロートしている必要があります。  

# 手順

## 0. 注意事項

* **測定環境:** 温度変化などにより抵抗値や回路特性が変動する可能性があるため、安定した環境で測定を行ってください。
* **測定確度:** 使用する計測機器の測定確度がキャリブレーション結果に直接影響します。
## 1. setup
### 本装置を出力固定モードに変更する
本体のUI基板上にある「TEST/NORMAL」切り替えジャンパを「TEST」側に設定します。これにより駆動チャネルが固定されます。 
固定されるチャネルは回路図上の表記で「DRIVE_13」となり、SCSIコネクタ上では「13,38」のペアになります。  
（写真）
### 駆動電流値を設定する
測定する駆動電流をフロントパネルから設定します。
### コイルドライブ出力コネクタに終端抵抗取り付け用のジグを接続
装置の裏側のコネクタに終端抵抗取り付け用のジグを接続します。ここではMEG用の周辺部品として手元にあった、SCSIコネクタをBNCコネクタに接続するジグと、SCSIケーブルを使用しました。  
(写真)

### 動作確認
装置の電源を入れ動作させます。終端抵抗取り付けるジグの端子から信号が連続して出ていることをオシロスコープで確認します。  

## 2. 計測
### 終端抵抗の抵抗値計測
終端抵抗の抵抗値を計測します。可能であれば4端子法を用いて計測すると確度が高い値を得る事ができます。  
この値で駆動電流を算出することになります。

### モニタ出力と終端抵抗両端の電圧計測
抵抗値を確認した終端抵抗をコイルドライブ出力コネクタに接続したジグに装着し、コイルのダミーとして動作させます。  
この終端抵抗の両端をFFTアナライザの入力に導入し、コイルに流れている実際の電流値として計測します。  
同時にモニタ出力端子をFFTアナライザの入力に導入し、コイルに流れている電流を装置で検出した結果として計測します。  
FFTには駆動周波数（標準では80Hz）にピークがある信号が検出されているので、そのピーク値を信号電圧とします。  
必要に応じて、平均化などを行い安定した測定値を得てください。

### 変換係数の算出
上記で得られた、終端抵抗の両端の電圧(Vr)とモニタ出力端子の電圧(Vm)、終端抵抗の値(Rt)から変換係数を算出します。  
コイルに流れている電流をId、求めたい電流電圧変換係数をkとすると

```math
\begin{aligned}
  &V_r=I_d R_t\\
  &V_m=k I_d\\
\end{aligned}
```
 ここから、

```math
k=\frac{V_m R_t}{V_r}
```

となるので、この式から電流電圧変換係数を計算します。
設計値は5033[V/A]です。（実質的に単位は[Ω]ですが、わかりやすさのため[V/A]としておきます）

### コイルに流れる電流値を測定
ここまでの計測はモニタ出力の電圧とコイルに流れる電流の関係を把握するための計測でしたが、電流検出のためにコイルの代わりに100Ωの終端抵抗をもちいたため、実際の磁場発生のためのコイルを接続した時に流れる電流値とは異なります。ここでは終端抵抗を0Ωにしてコイルに流れる電流値を確認します。  
終端抵抗を取り外し0Ωの抵抗に取り替え、実際のコイルが接続されたのと同様の状況を再現します。これにより実際のコイルに流れる電流値をモニタ出力端子の電圧の計測により算出します。  
この計測で、実際のコイルの駆動電流が意図した通りに実現されているかどうか判断します。

# まとめ
この作業でコイルドライバ回路のモニタ出力電圧に対して値づけ（電流ー電圧変換係数の実測）を行いました。これにより、モニタ出力電圧からコイルに流れている電流値を計算できるようになりました。また、コイルに流れる電流値が設計が意図している電流値であることを確認する事ができました。

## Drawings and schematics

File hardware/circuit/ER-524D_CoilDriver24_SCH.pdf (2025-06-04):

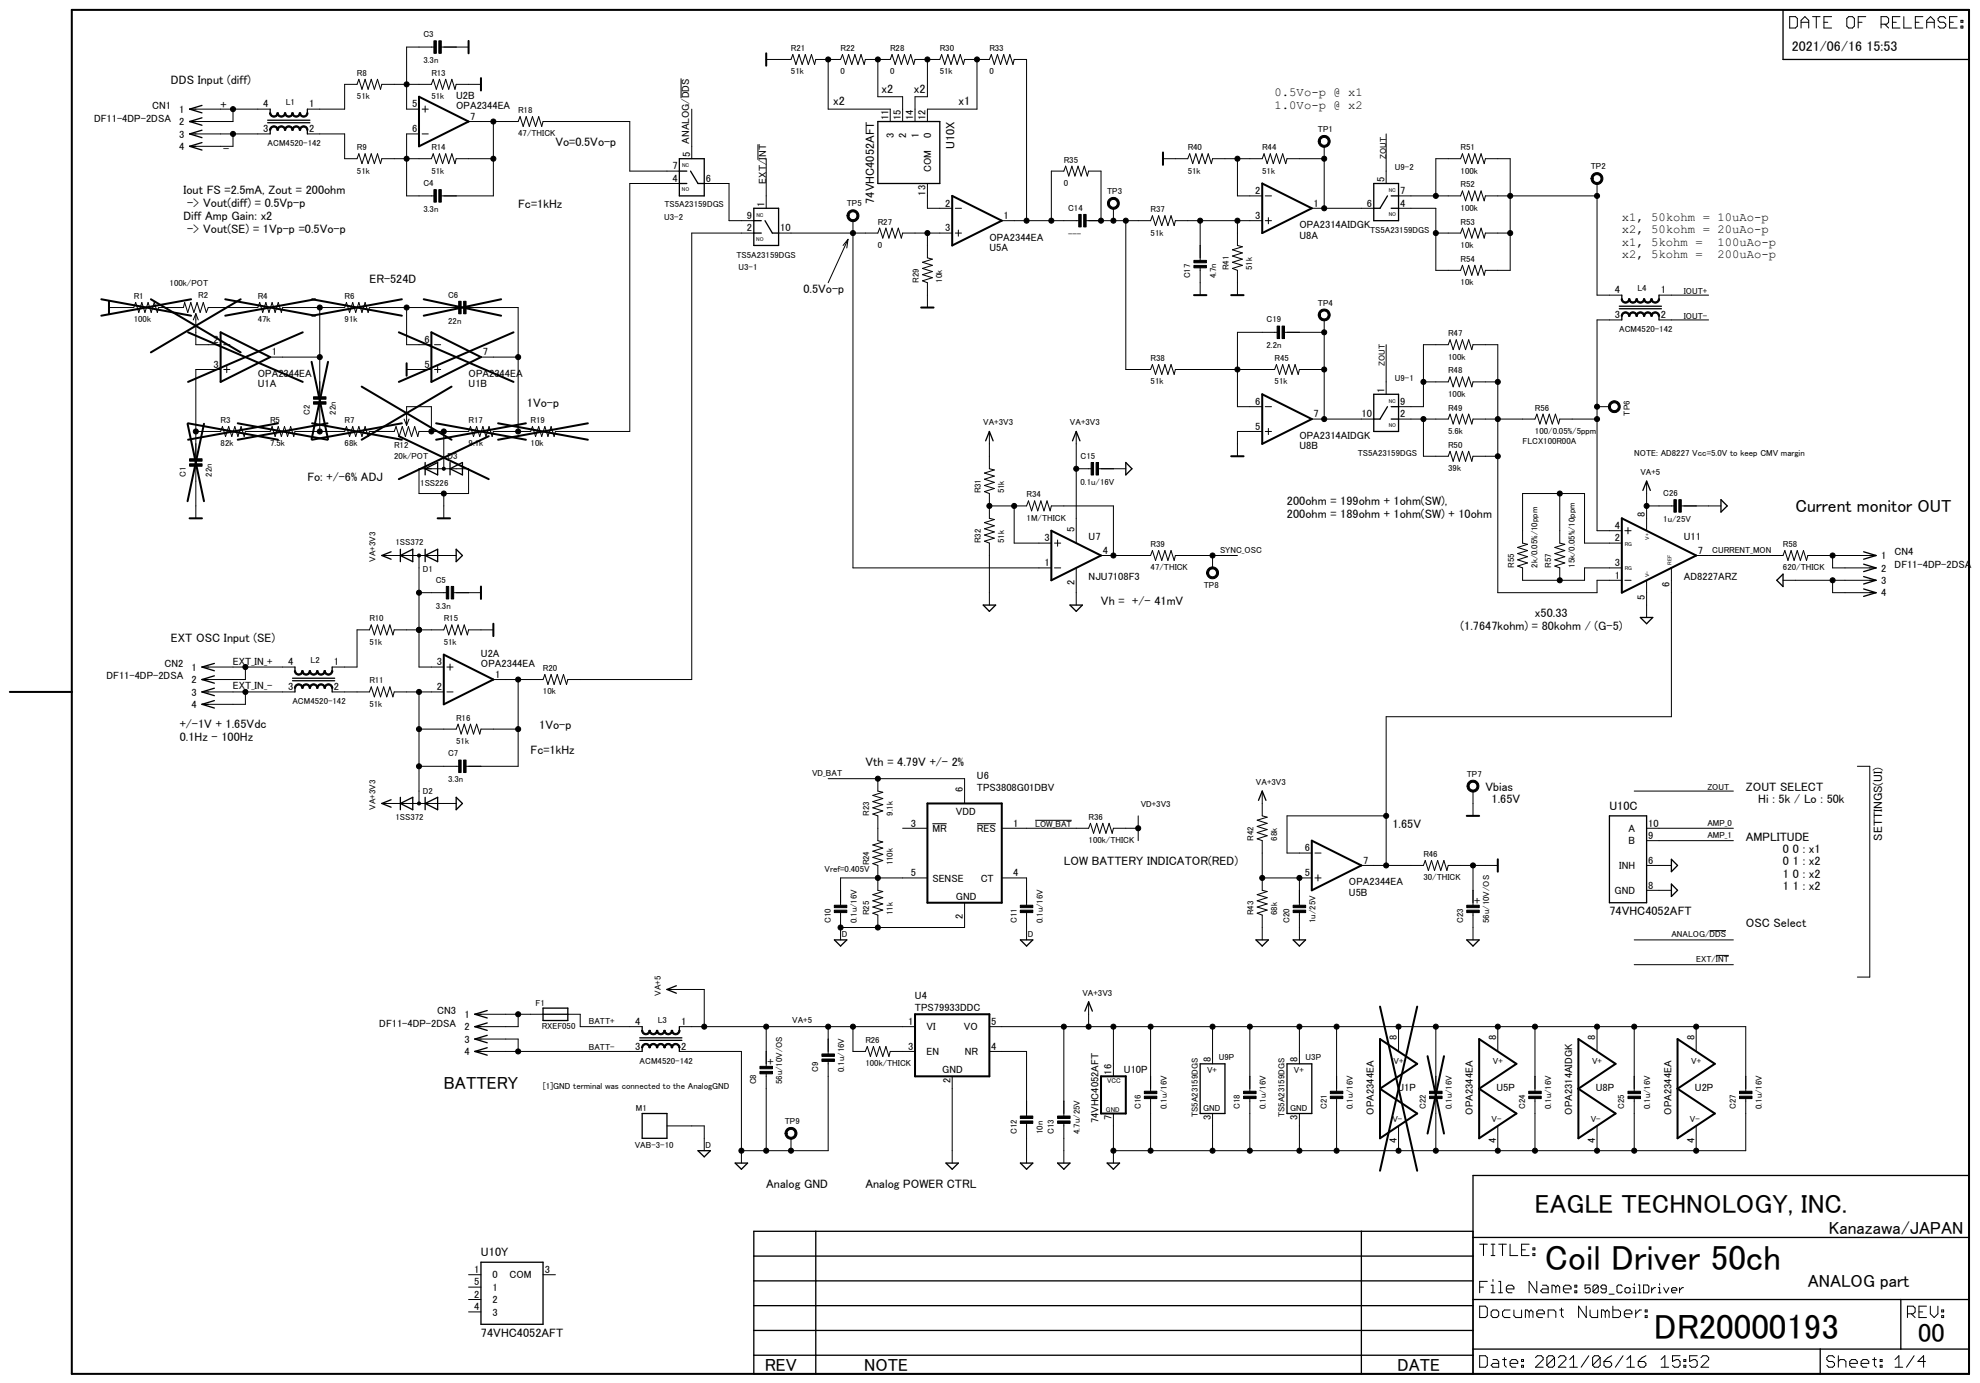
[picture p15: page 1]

Iout FS =2.5mA, Zout = 200ohm
-> Vout(diff) = 0.5Vp-p Diff Amp Gain: x2

NOTE: AD8227 Vcc=5.0V to keep CMV margin

EXT OSC Input (SE)

100k/THICK
LOW BATTERY INDICATOR(RED)

EAGLE TECHNOLOGY, INC. Kanazawa/JAPAN
Coil Driver 50ch

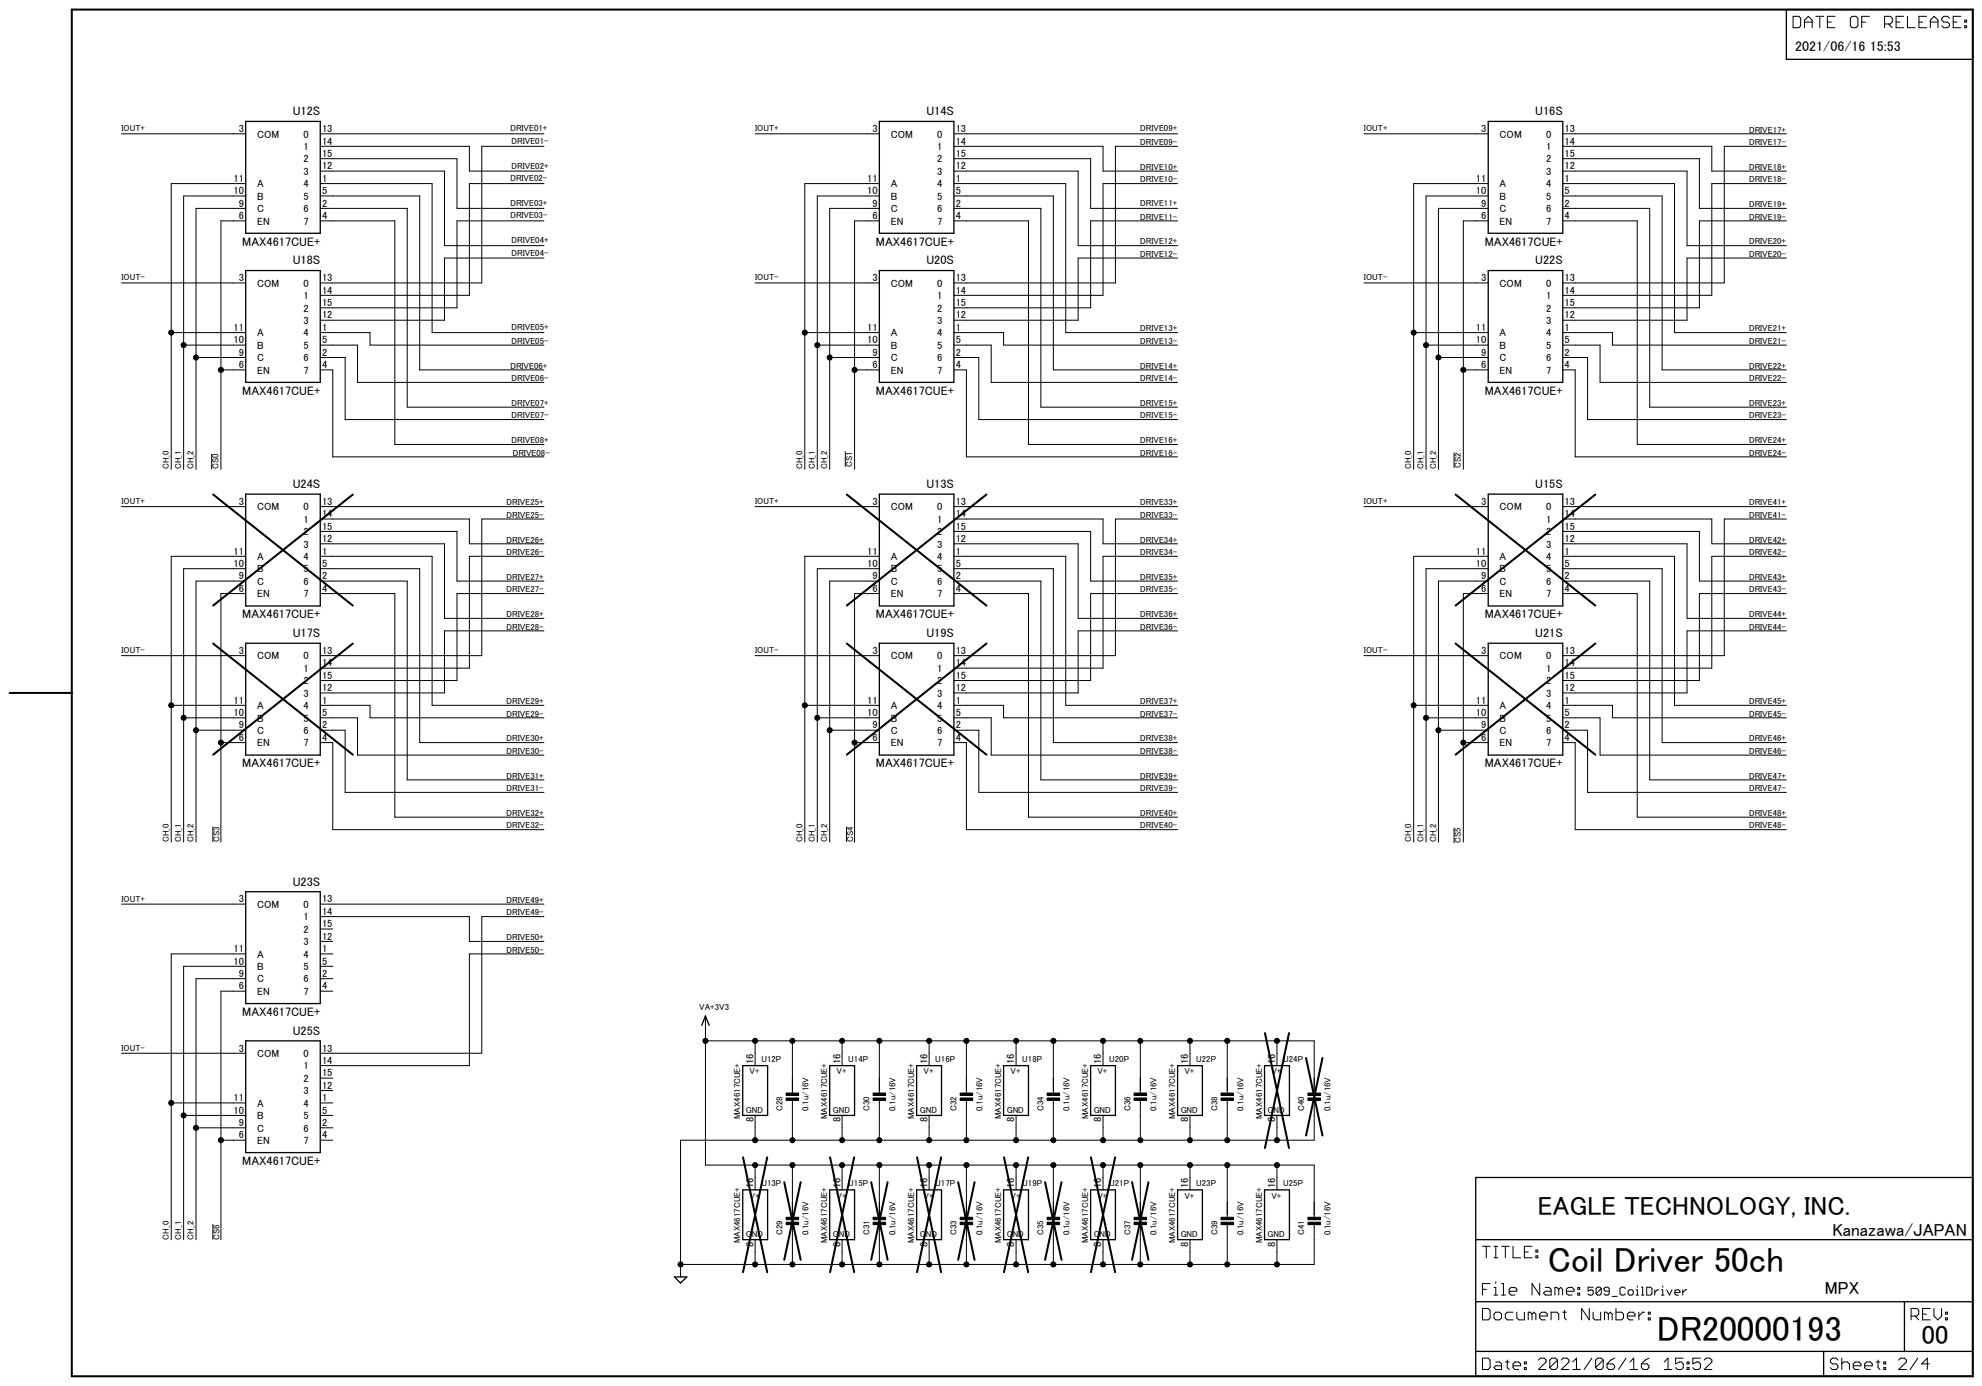
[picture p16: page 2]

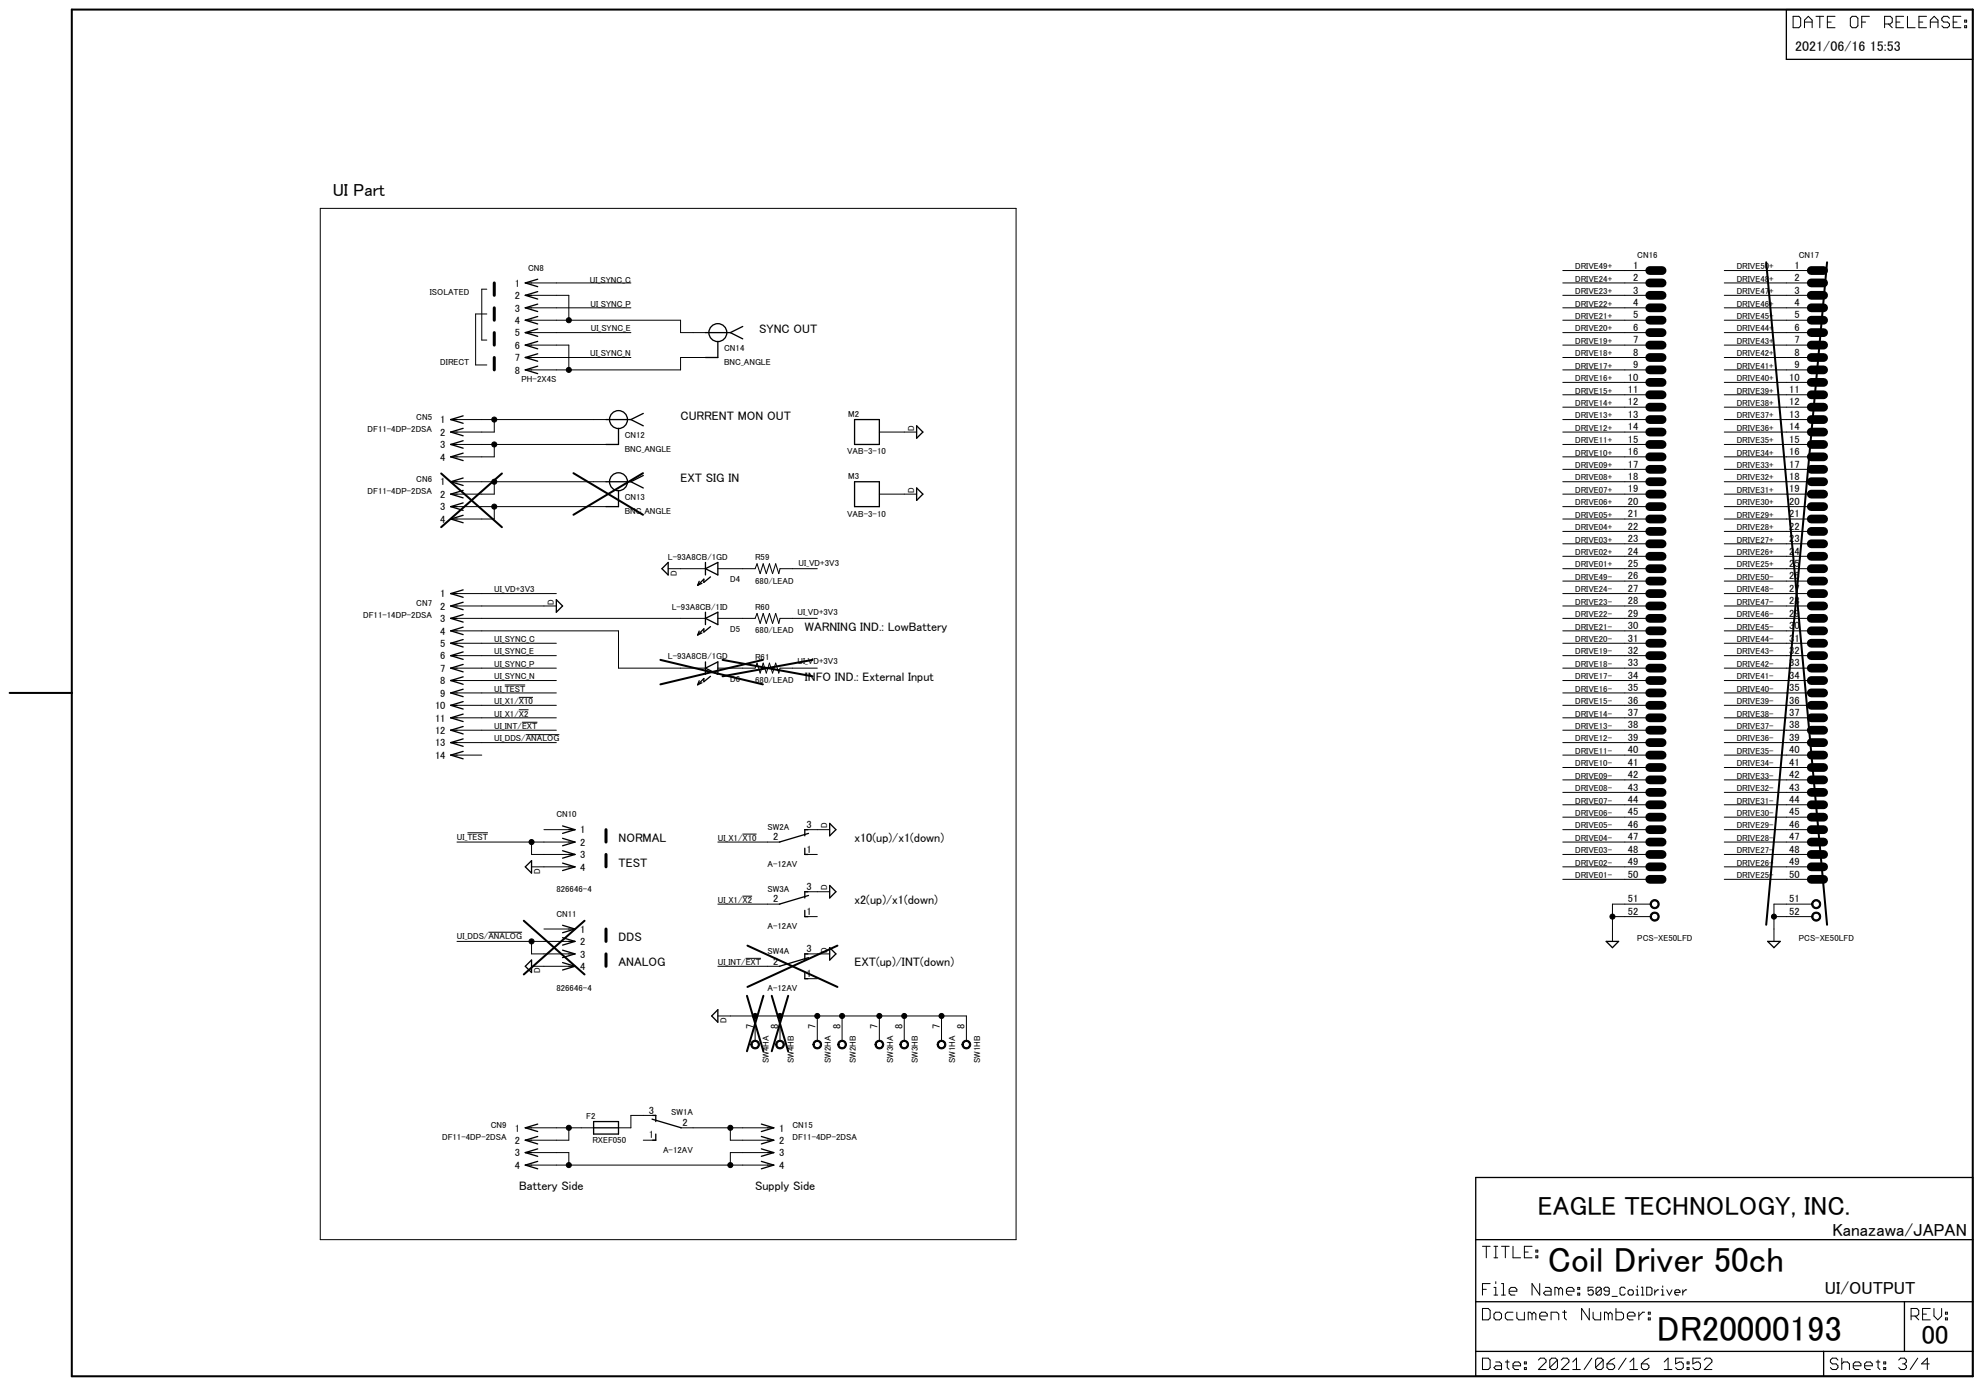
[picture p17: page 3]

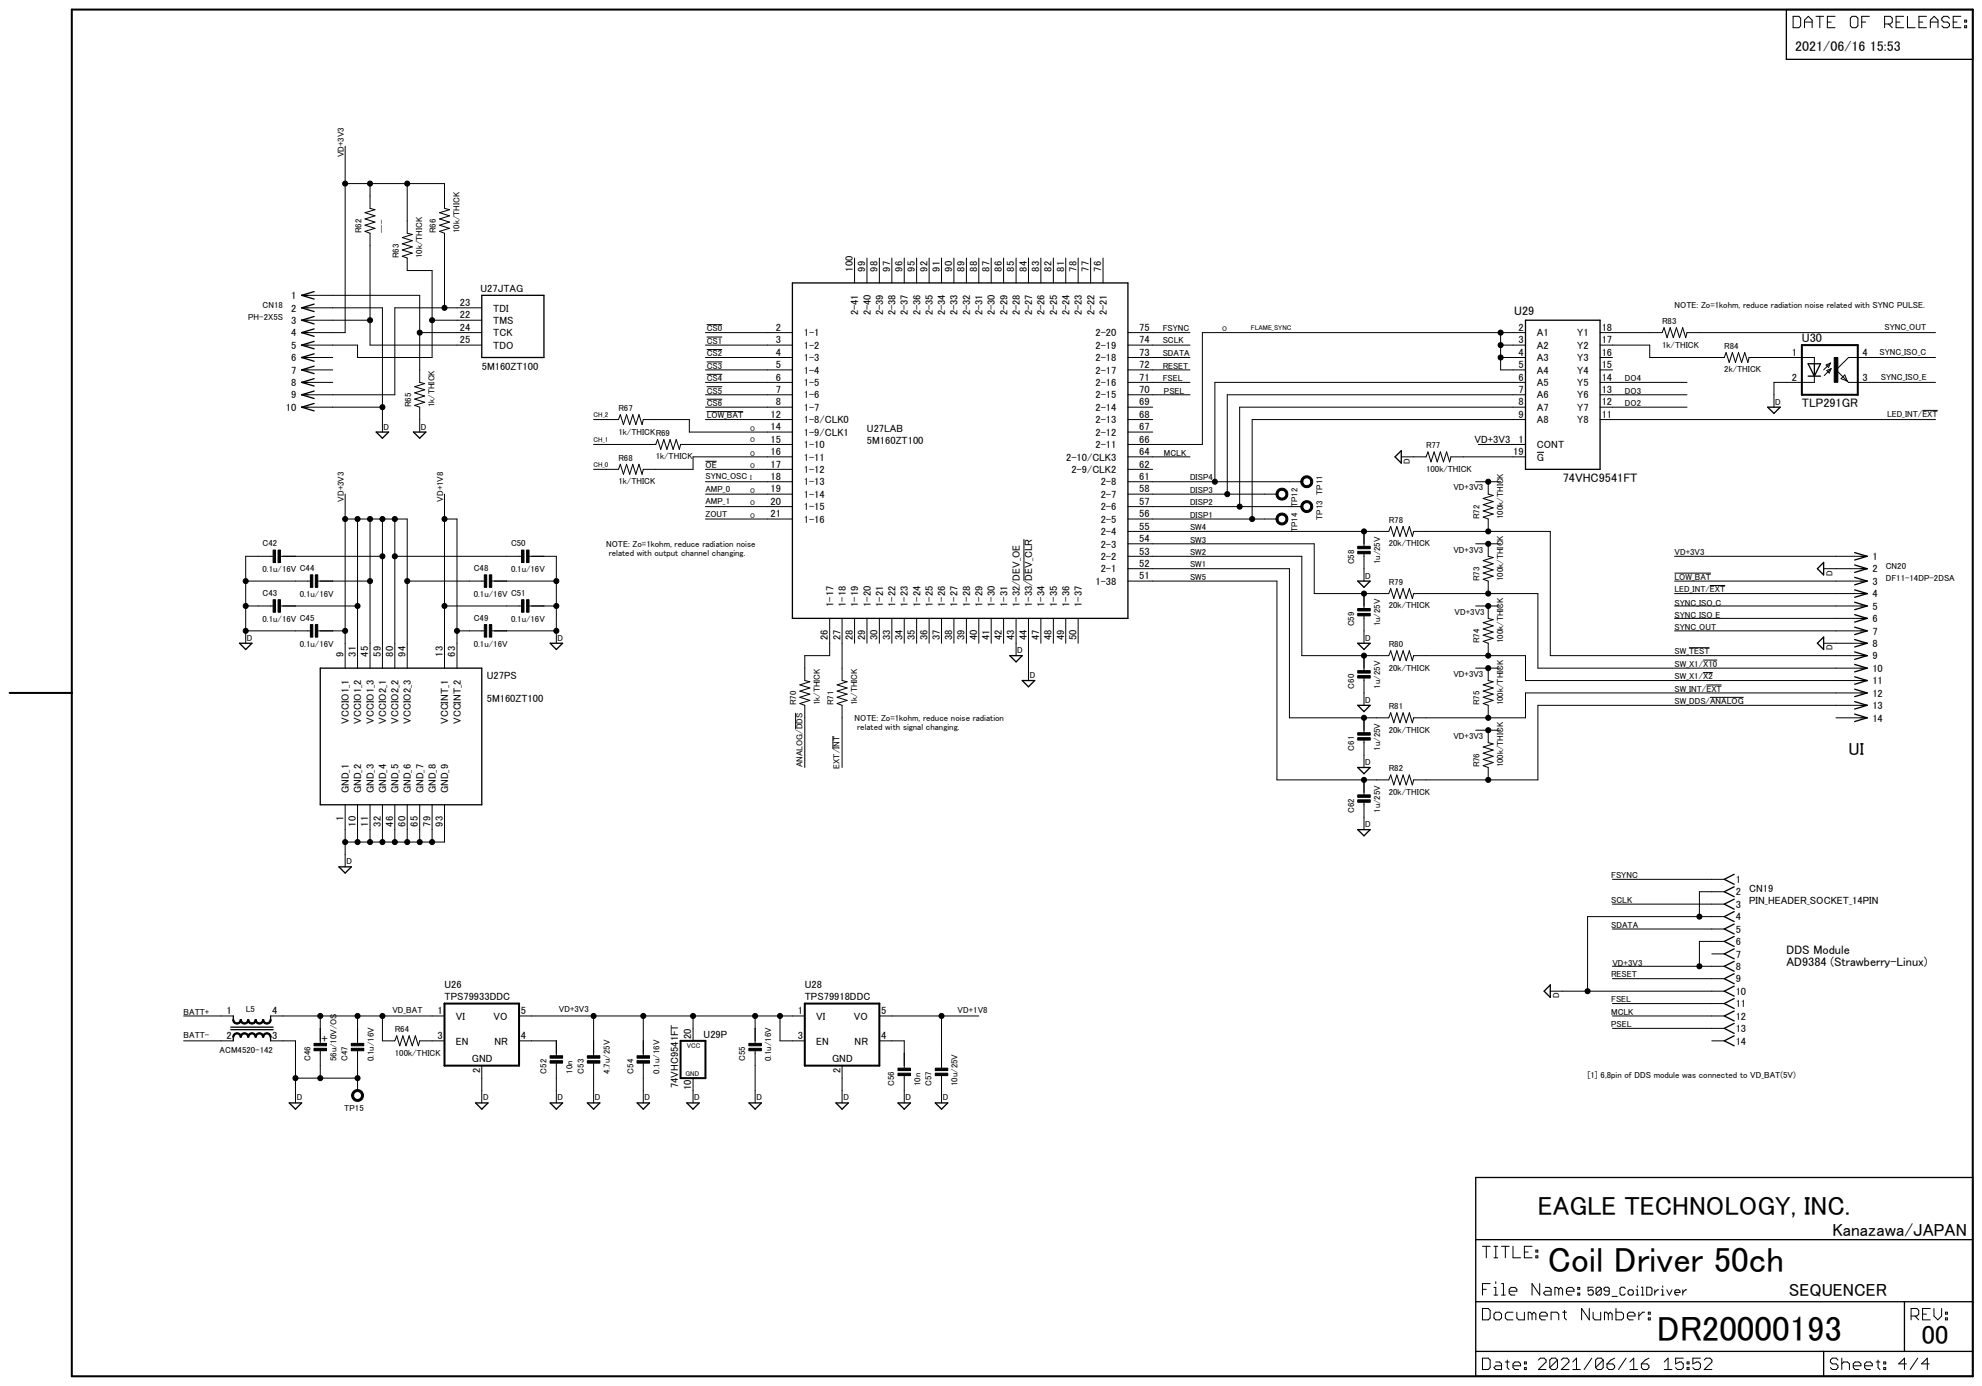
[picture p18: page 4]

NOTE: Zo=1kohm, reduce radiation noise related with SYNC PULSE.

NOTE: Zo=1kohm, reduce radiation noise
related with output channel changing.

EXT/INT ANALOG/DDS

NOTE: Zo=1kohm, reduce noise radiation
related with signal changing.

DDS Module AD9384 (Strawberry-Linux)

[1] 6,8pin of DDS module was connected to VD_BAT(5V)

EAGLE TECHNOLOGY, INC. Kanazawa/JAPAN
Coil Driver 50ch

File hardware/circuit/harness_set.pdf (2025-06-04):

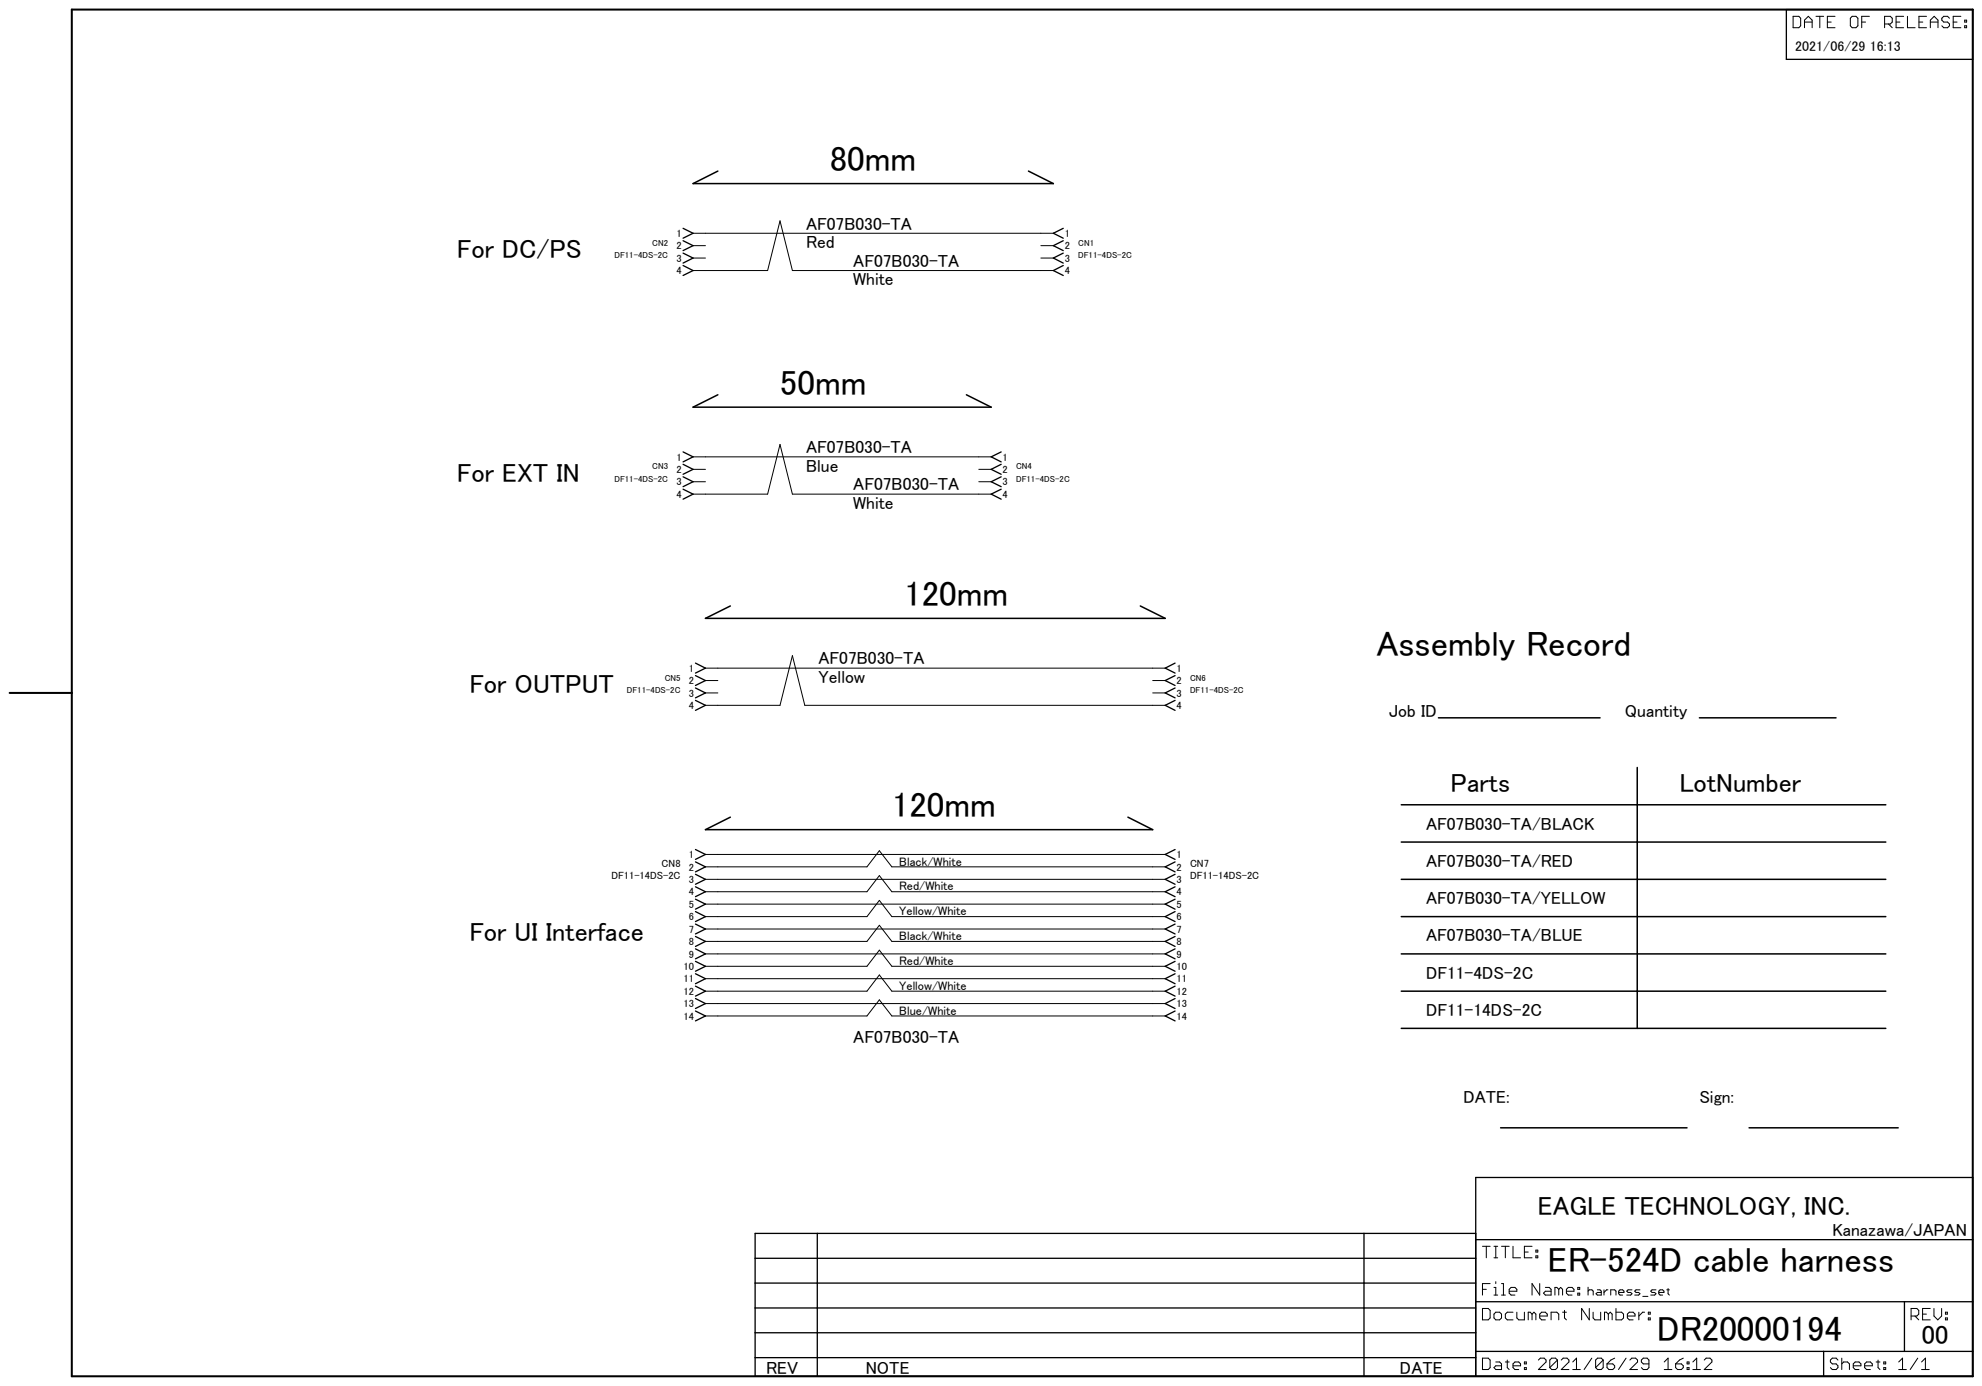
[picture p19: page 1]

Black/White Red/White Yellow/White Black/White Red/White Yellow/White Blue/White

EAGLE TECHNOLOGY, INC. Kanazawa/JAPAN
ER-524D cable harness

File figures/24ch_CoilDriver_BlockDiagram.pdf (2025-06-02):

## DDS

80Hz

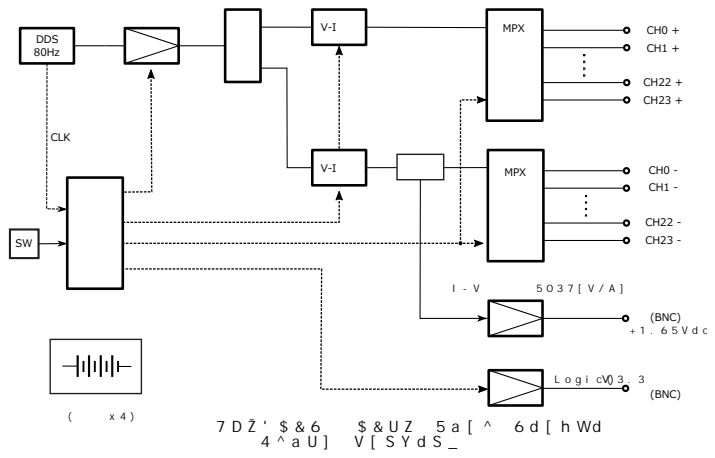
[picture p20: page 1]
シーケンス・コントロール回路; アンプ; 差動ドライバ; V-I変換; MPX; チャネル設定; 電流設定; 電流検出; I-V変換係数：5037[V/A]; +1.65Vdc=0A; 出力電流モニタ (BNC); CLK; Logic(3.3 V); 同期信号; (BNC); 電源 (単三型x4)

&3%DI$PJM%SJWFS
#MPDLEJBHSBN

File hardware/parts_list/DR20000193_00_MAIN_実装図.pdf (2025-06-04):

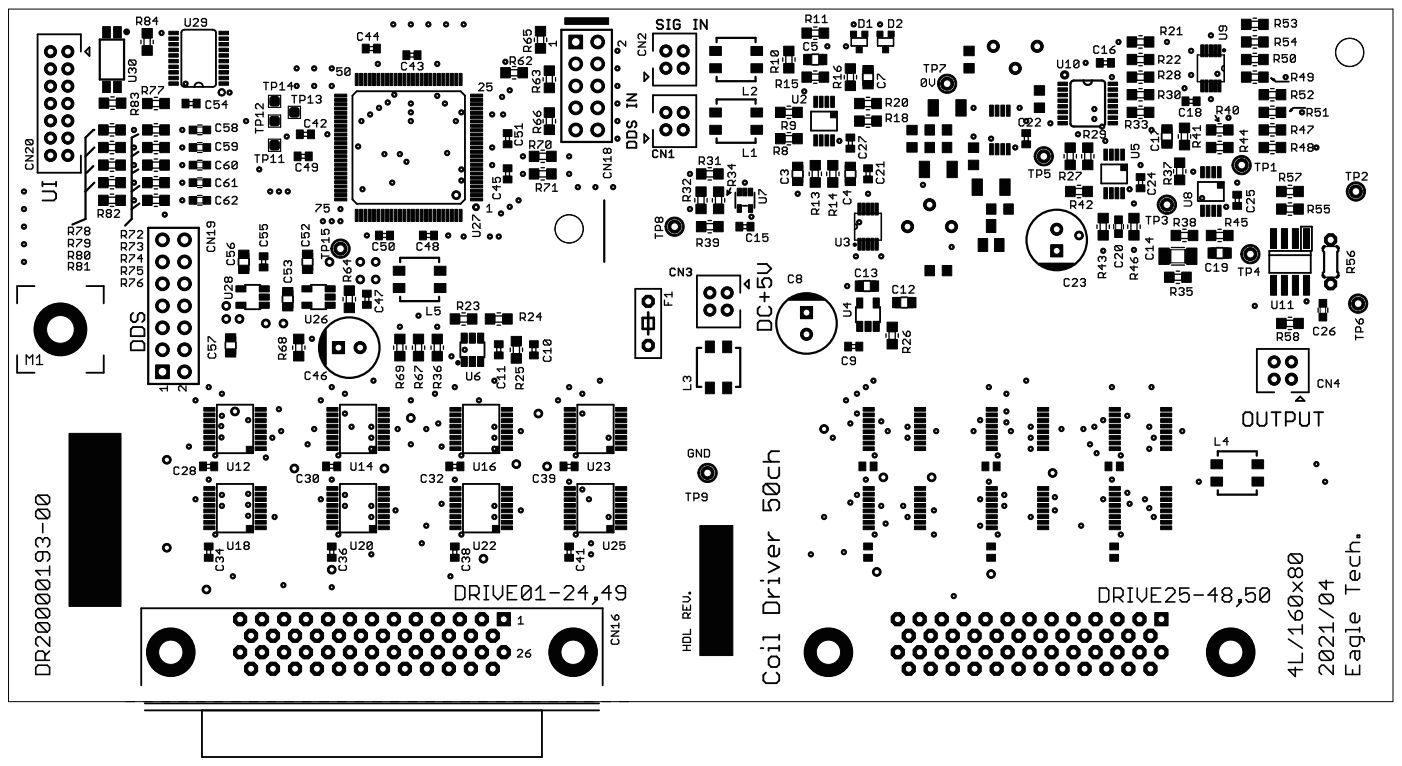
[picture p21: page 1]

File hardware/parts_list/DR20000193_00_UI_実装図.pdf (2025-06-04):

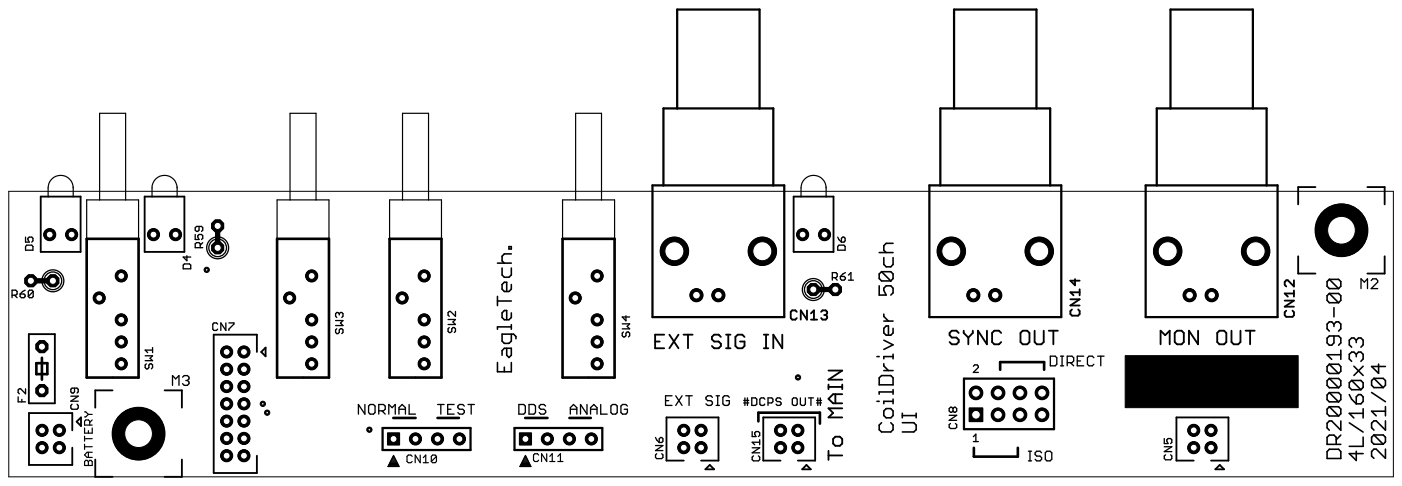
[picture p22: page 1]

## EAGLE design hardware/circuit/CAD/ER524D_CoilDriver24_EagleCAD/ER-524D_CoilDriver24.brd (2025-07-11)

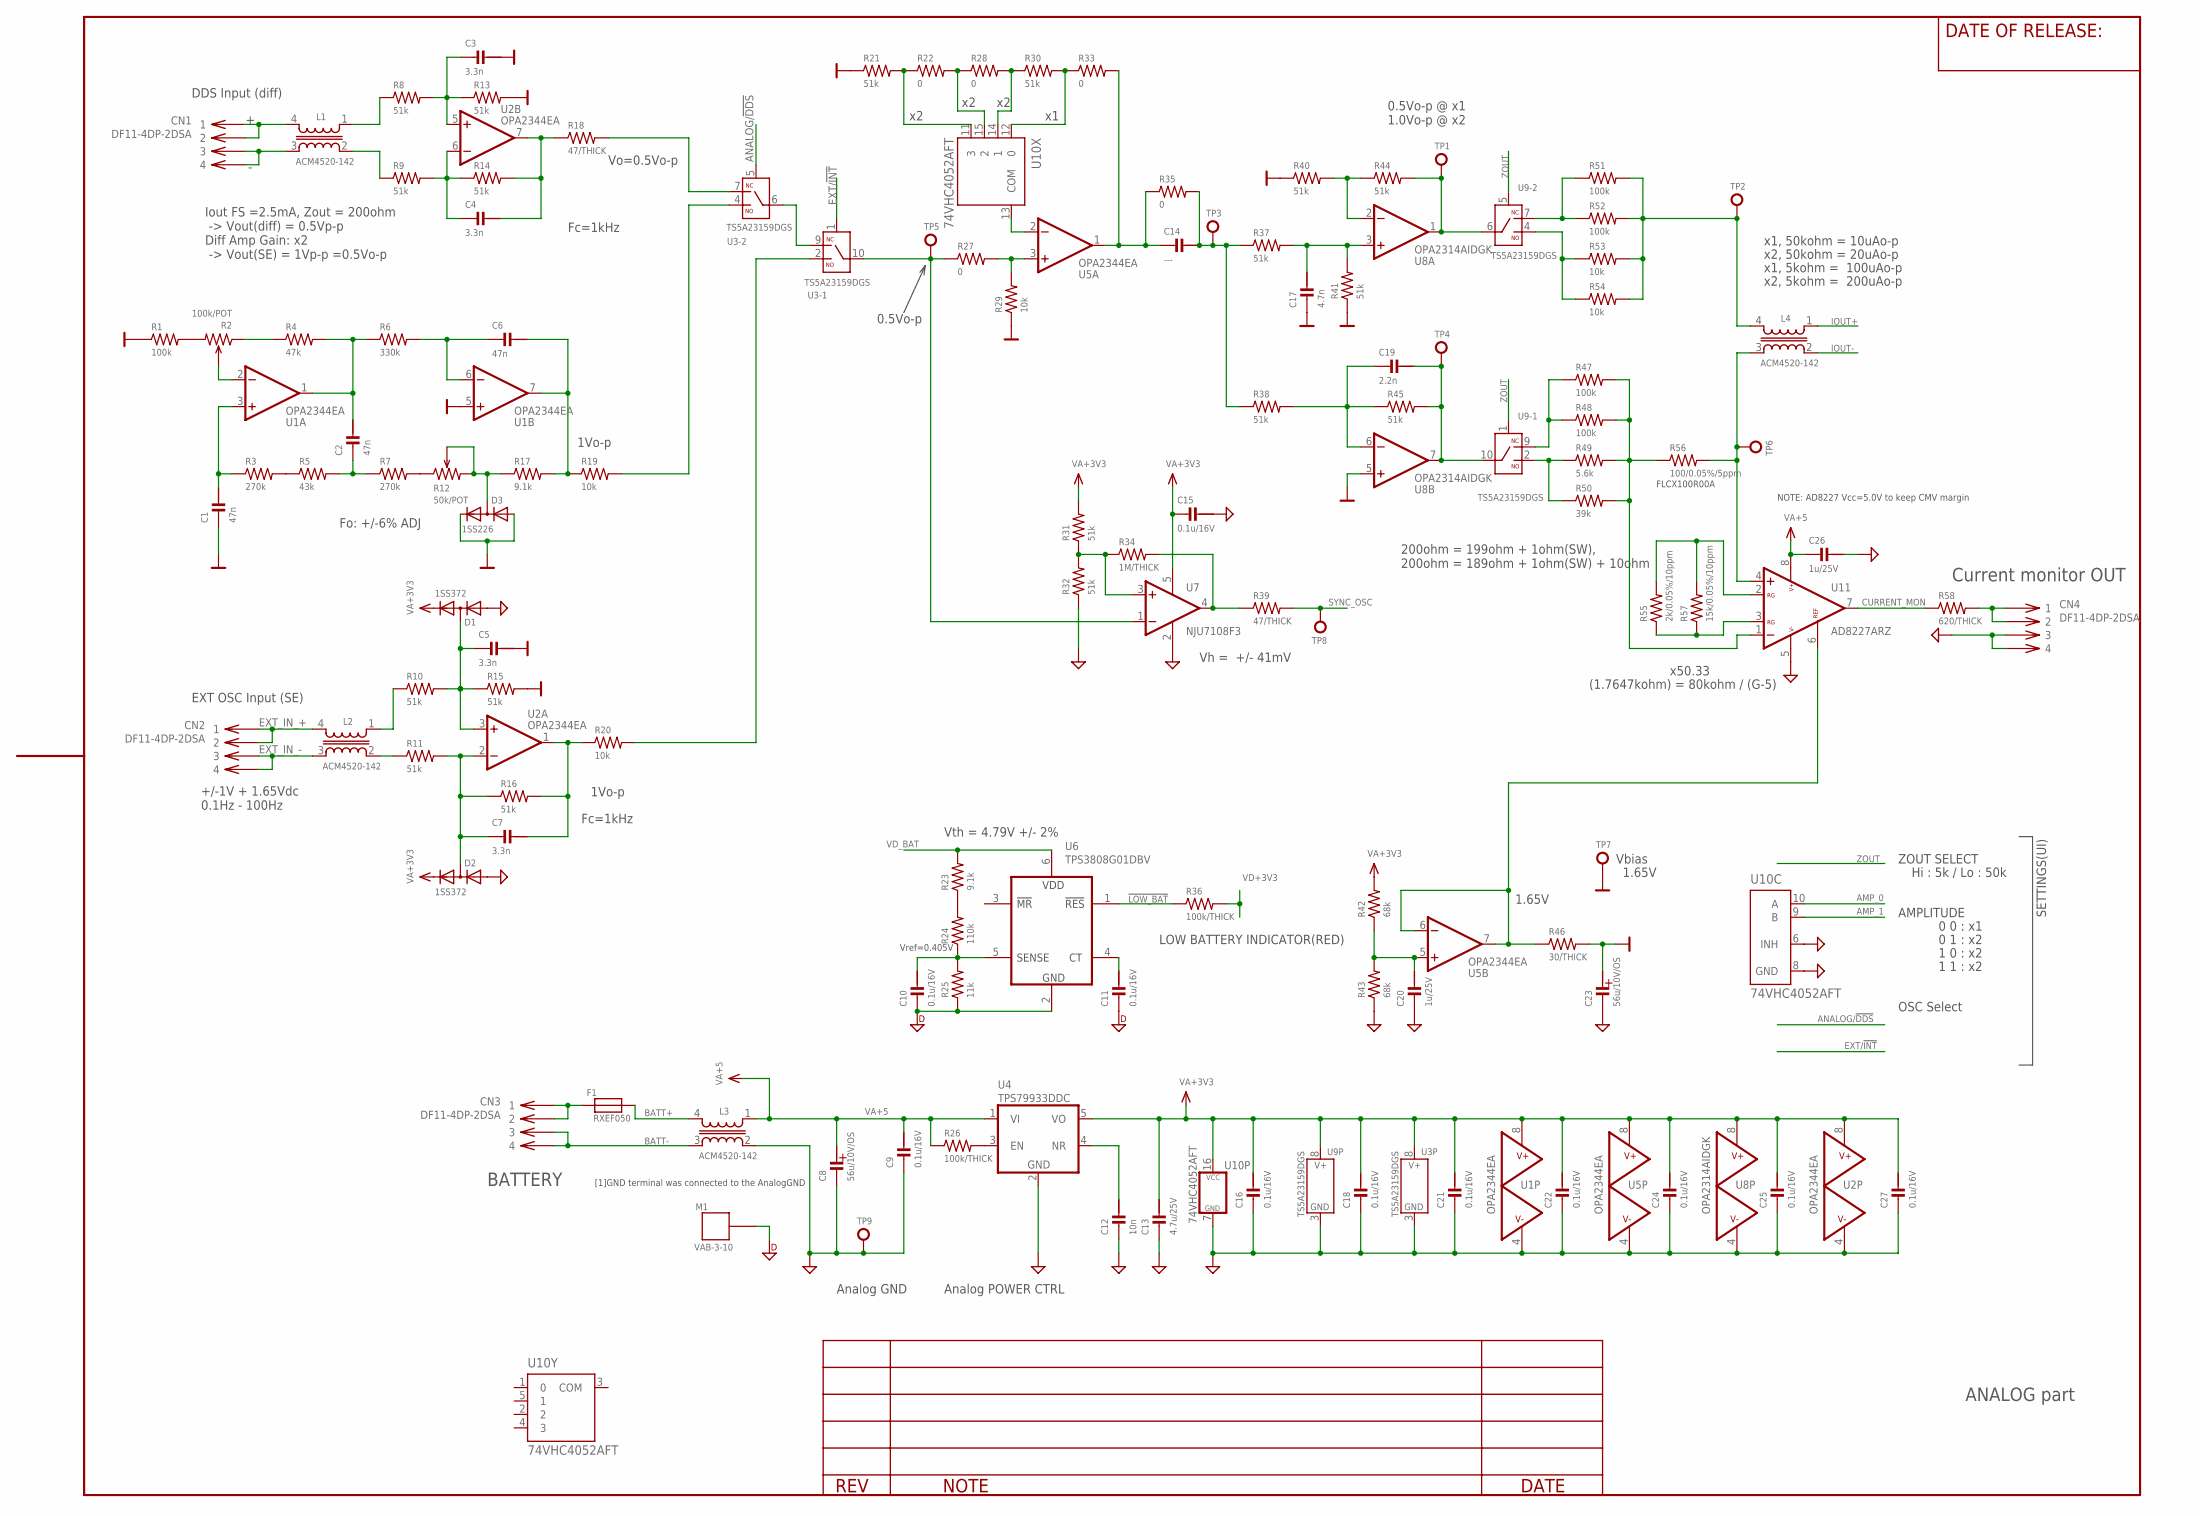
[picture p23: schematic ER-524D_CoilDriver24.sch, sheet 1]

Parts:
C1, C2, C6: 47n; CM3216
C3, C4, C5, C7: 3.3n; CM2012
C8, C23: 56u/10V/OS; PHI_6.3
C9, C10, C11, C15, C16, C18, C21, C22, C24, C25, C27: 0.1u/16V; CM1005
C12: 10n; CM2012
C13: 4.7u/25V; CM2012
C14: ---; CM3216
C17: 4.7n; CM2012
C19: 2.2n; CM2012
C20, C26: 1u/25V; CM1608
CN1, CN2, CN3, CN4: DF11-4DP-2DSA
D1, D2: 1SS372; SC70-3-R
D3: 1SS226; SOT23
F1: RXEF050; 8X3/5.08
L1, L2, L3, L4: ACM4520-142; ACM4520
M1: VAB-3-10; VAB_3_10_CONTACT
R1, R47, R48, R51, R52: 100k; RM1608
R2: 100k/POT; CT-6
R3, R7: 270k; RM1608
R4: 47k; RM1608
R5: 43k; RM1608
R6: 330k; RM1608
R8, R9, R10, R11, R13, R14, R15, R16, R21, R30, R31, R32, R37, R38, R40, R41, R44, R45: 51k; RM1608
R12: 50k/POT; CT-6
R17, R23: 9.1k; RM1608
R18, R39: 47/THICK; RM1608
R19, R20, R29, R53, R54: 10k; RM1608
R22, R27, R28, R33, R35: 0; RM1608
R24: 110k; RM1608
R25: 11k; RM1608
R26, R36: 100k/THICK; RM1608
R34: 1M/THICK; RM1608
R42, R43: 68k; RM1608
R46: 30/THICK; RM1608
R49: 5.6k; RM1608
R50: 39k; RM1608
R55: 2k/0.05%/10ppm; RM1608
R56: 100/0.05%/5ppm; 0204/5
R57: 15k/0.05%/10ppm; RM1608
R58: 620/THICK; RM1608
TP1, TP2, TP3, TP4, TP5, TP6, TP7, TP8, TP9: TP-LC3G; TP_TH_0R9MM
U1, U2, U5: OPA2344EA; MSO8_AEL
U3, U9: TS5A23159DGS; MSOP10
U4: TPS79933DDC; SOT-23-5
U6: TPS3808G01DBV; SOT-23
U7: NJU7108F3; SC88A
U8: OPA2314AIDGK; MSO8_AEL
U10: 74VHC4052AFT; TSSOP16-P-044-065A
U11: AD8227ARZ; SO8_AEL

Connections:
0V: C1.2, C3.1, C5.1, C17.2, C23.POS, D3.1 (A), D3.2 (C), R1.1, R13.2, R15.2, R21.1, R29.1, R40.1, R41.1, R46.2, TP7.1, U1.5 (+IN), U8.5 (+IN)
80_POWER: R26.2, U4.3 (EN)
!LOW_BAT: R36.1, U6.1 (!RESET); also elsewhere on the board
AGND: C8.NEG, C9.2, C12.2, C13.2, C15.1, C16.2, C18.2, C20.2, C21.2, C22.2, C23.NEG, C24.2, C25.2, C26.1, C27.2, CN4.3, CN4.4, D1.1 (A), D2.1 (A), L3.2 (3), R32.1, R43.1, TP9.1, U1.4 (V-), U2.4 (V-), U3.3 (V-), U4.2 (GND), U5.4 (V-), U7.2 (V-), U8.4 (V-), U9.3 (V-), U10.6 (INH), U10.7 (GND), U10.8 (GND), U11.5 (V-); also elsewhere on the board
AMP_0: U10.10 (A); also elsewhere on the board
AMP_1: U10.9 (B); also elsewhere on the board
ANALOG/!DDS!: U3.5 (IN); also elsewhere on the board
BATT+: F1.2, L3.4 (2); also elsewhere on the board
BATT-: CN3.3, CN3.4, L3.3 (4); also elsewhere on the board
CURRENT_MON: R58.1, U11.7 (OUT)
DGND: C10.2, C11.2, M1.CASE1, R25.1, U6.2 (GND); also elsewhere on the board
EXT/!INT!: U3.1 (IN); also elsewhere on the board
EXT_IN_+: CN2.1, CN2.2, L2.4 (2)
EXT_IN_-: CN2.3, CN2.4, L2.3 (4)
IOUT+: L4.1; also elsewhere on the board
IOUT-: L4.2 (3); also elsewhere on the board
unnamed: L2.1, R10.1
unnamed: U3.6 (COM), U3.9 (NC)
unnamed: R7.2, R12.1
unnamed: C3.2, R8.2, R13.1, U2.5 (+IN)
unnamed: R1.2, R2.3
unnamed: C7.2, D2.3 (AC), R11.2, R16.1, U2.2 (-IN)
unnamed: C6.1, R17.2, R19.1, U1.7 (OUT)
unnamed: L4.4 (2), R51.2, R52.2, R53.2, R54.2, TP2.1
unnamed: R21.2, R22.1, U10.11 (3)
unnamed: C7.1, R16.2, R20.1, U2.1 (OUT)
unnamed: R22.2, R28.1, U10.15 (2)
unnamed: R28.2, R30.1, U10.14 (1)
unnamed: C5.2, D1.3 (AC), R10.2, R15.1, U2.3 (+IN)
unnamed: L1.2 (3), R9.1
unnamed: R30.2, R33.1, U10.12 (0)
unnamed: C20.1, R42.1, R43.2, U5.5 (+IN)
unnamed: C19.2, R38.2, R45.1, U8.6 (-IN)
unnamed: U5.2 (-IN), U10.13 (COM)
unnamed: C14.2, R33.2, R35.1, U5.1 (OUT)
unnamed: R27.2, R29.2, U5.3 (+IN)
unnamed: C19.1, R45.2, TP4.1, U8.7 (OUT), U9.10 (COM)
unnamed: R44.2, TP1.1, U8.1 (OUT), U9.6 (COM)
unnamed: R40.2, R44.1, U8.2 (-IN)
unnamed: C17.1, R37.2, R41.2, U8.3 (+IN)
unnamed: R49.1, R50.1, U9.2 (NO)
unnamed: R47.1, R48.1, U9.9 (NC)
unnamed: R47.2, R48.2, R49.2, R50.2, R56.1, U11.1 (-IN)
unnamed: R51.1, R52.1, U9.7 (NC)
unnamed: R53.1, R54.1, U9.4 (NO)
unnamed: C4.1, R14.2, R18.1, U2.7 (OUT)
unnamed: R2.1, R4.1
unnamed: C2.1, R4.2, R6.1, U1.1 (OUT)
unnamed: C6.2, R6.2, U1.6 (-IN)
unnamed: R2.2, U1.2 (-IN)
unnamed: C1.1, R3.1, U1.3 (+IN)
unnamed: R3.2, R5.1
unnamed: C2.2, R5.2, R7.1
unnamed: D3.3 (AC), R12.2, R12.3, R17.1
unnamed: C14.1, R35.2, R37.1, R38.1, TP3.1
unnamed: L4.3 (4), R56.2, TP6.1, U11.4 (+IN)
unnamed: C4.2, R9.2, R14.1, U2.6 (-IN)
unnamed: CN1.3, CN1.4, L1.3 (4)
unnamed: CN1.1, CN1.2, L1.4 (2)
unnamed: R31.1, R32.2, R34.1, U7.3 (+IN)
unnamed: R34.2, R39.1, U7.4 (OUT)
unnamed: CN3.1, CN3.2, F1.1
unnamed: C11.1, U6.4 (CT)
unnamed: L1.1, R8.1
unnamed: C10.1, R24.1, R25.2, U6.5 (SENSE)
unnamed: CN4.1, CN4.2, R58.2
unnamed: C12.1, U4.4 (NR)
unnamed: L2.2 (3), R11.1
unnamed: R20.2, U3.2 (NO)
unnamed: R18.2, U3.7 (NC)
unnamed: R27.1, TP5.1, U3.10 (COM), U7.1 (-IN)
unnamed: R19.2, U3.4 (NO)
unnamed: R23.1, R24.2
unnamed: R55.1, R57.1, U11.3 (RG2)
unnamed: R55.2, R57.2, U11.2 (RG1)
unnamed: R46.1, U5.6 (-IN), U5.7 (OUT), U11.6 (REF)
SYNC_OSC: R39.2, TP8.1; also elsewhere on the board
VA+3V3: C13.1, C15.2, C16.1, C18.1, C21.1, C22.1, C24.1, C25.1, C27.1, D1.2 (C), D2.2 (C), R31.2, R42.2, U1.8 (V+), U2.8 (V+), U3.8 (V+), U4.5 (VO), U5.8 (V+), U7.5 (V+), U8.8 (V+), U9.8 (V+), U10.16 (VCC); also elsewhere on the board
VA+5: C8.POS, C9.1, C26.2, L3.1, R26.1, U4.1 (VI), U11.8 (V+)
VD+3V3: R36.2; also elsewhere on the board
VD_BAT: R23.2, U6.6 (VDD); also elsewhere on the board
ZOUT: U9.1 (IN), U9.5 (IN); also elsewhere on the board

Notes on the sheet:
ANALOG part
AMPLITUDE
ZOUT SELECT
Hi : 5k / Lo : 50k
0 0 : x1
0 1 : x2
1 0 : x2
1 1 : x2
LOW BATTERY INDICATOR(RED)
Vth = 4.79V +/- 2%
Vref=0.405V
Analog GND
Analog POWER CTRL
1.65V
Vh = +/- 41mV
Vbias
Fo: +/-6% ADJ
x1, 50kohm = 10uAo-p
x2, 50kohm = 20uAo-p
x1, 5kohm = 100uAo-p
x2, 5kohm = 200uAo-p
0.5Vo-p
x50.33
DDS Input (diff)
Vo=0.5Vo-p
Fc=1kHz
[1]GND terminal was connected to the AnalogGND
BATTERY
Current monitor OUT
NOTE: AD8227 Vcc=5.0V to keep CMV margin
Iout FS =2.5mA, Zout = 200ohm -> Vout(diff) = 0.5Vp-p Diff Amp Gain: x2 -> Vout(SE) = 1Vp-p =0.5Vo-p
1Vo-p
EXT OSC Input (SE)
+/-1V + 1.65Vdc 0.1Hz - 100Hz
OSC Select
200ohm = 199ohm + 1ohm(SW), 200ohm = 189ohm + 1ohm(SW) + 10ohm
SETTINGS(UI)
0.5Vo-p @ x1 1.0Vo-p @ x2
(1.7647kohm) = 80kohm / (G-5)
FLCX100R00A

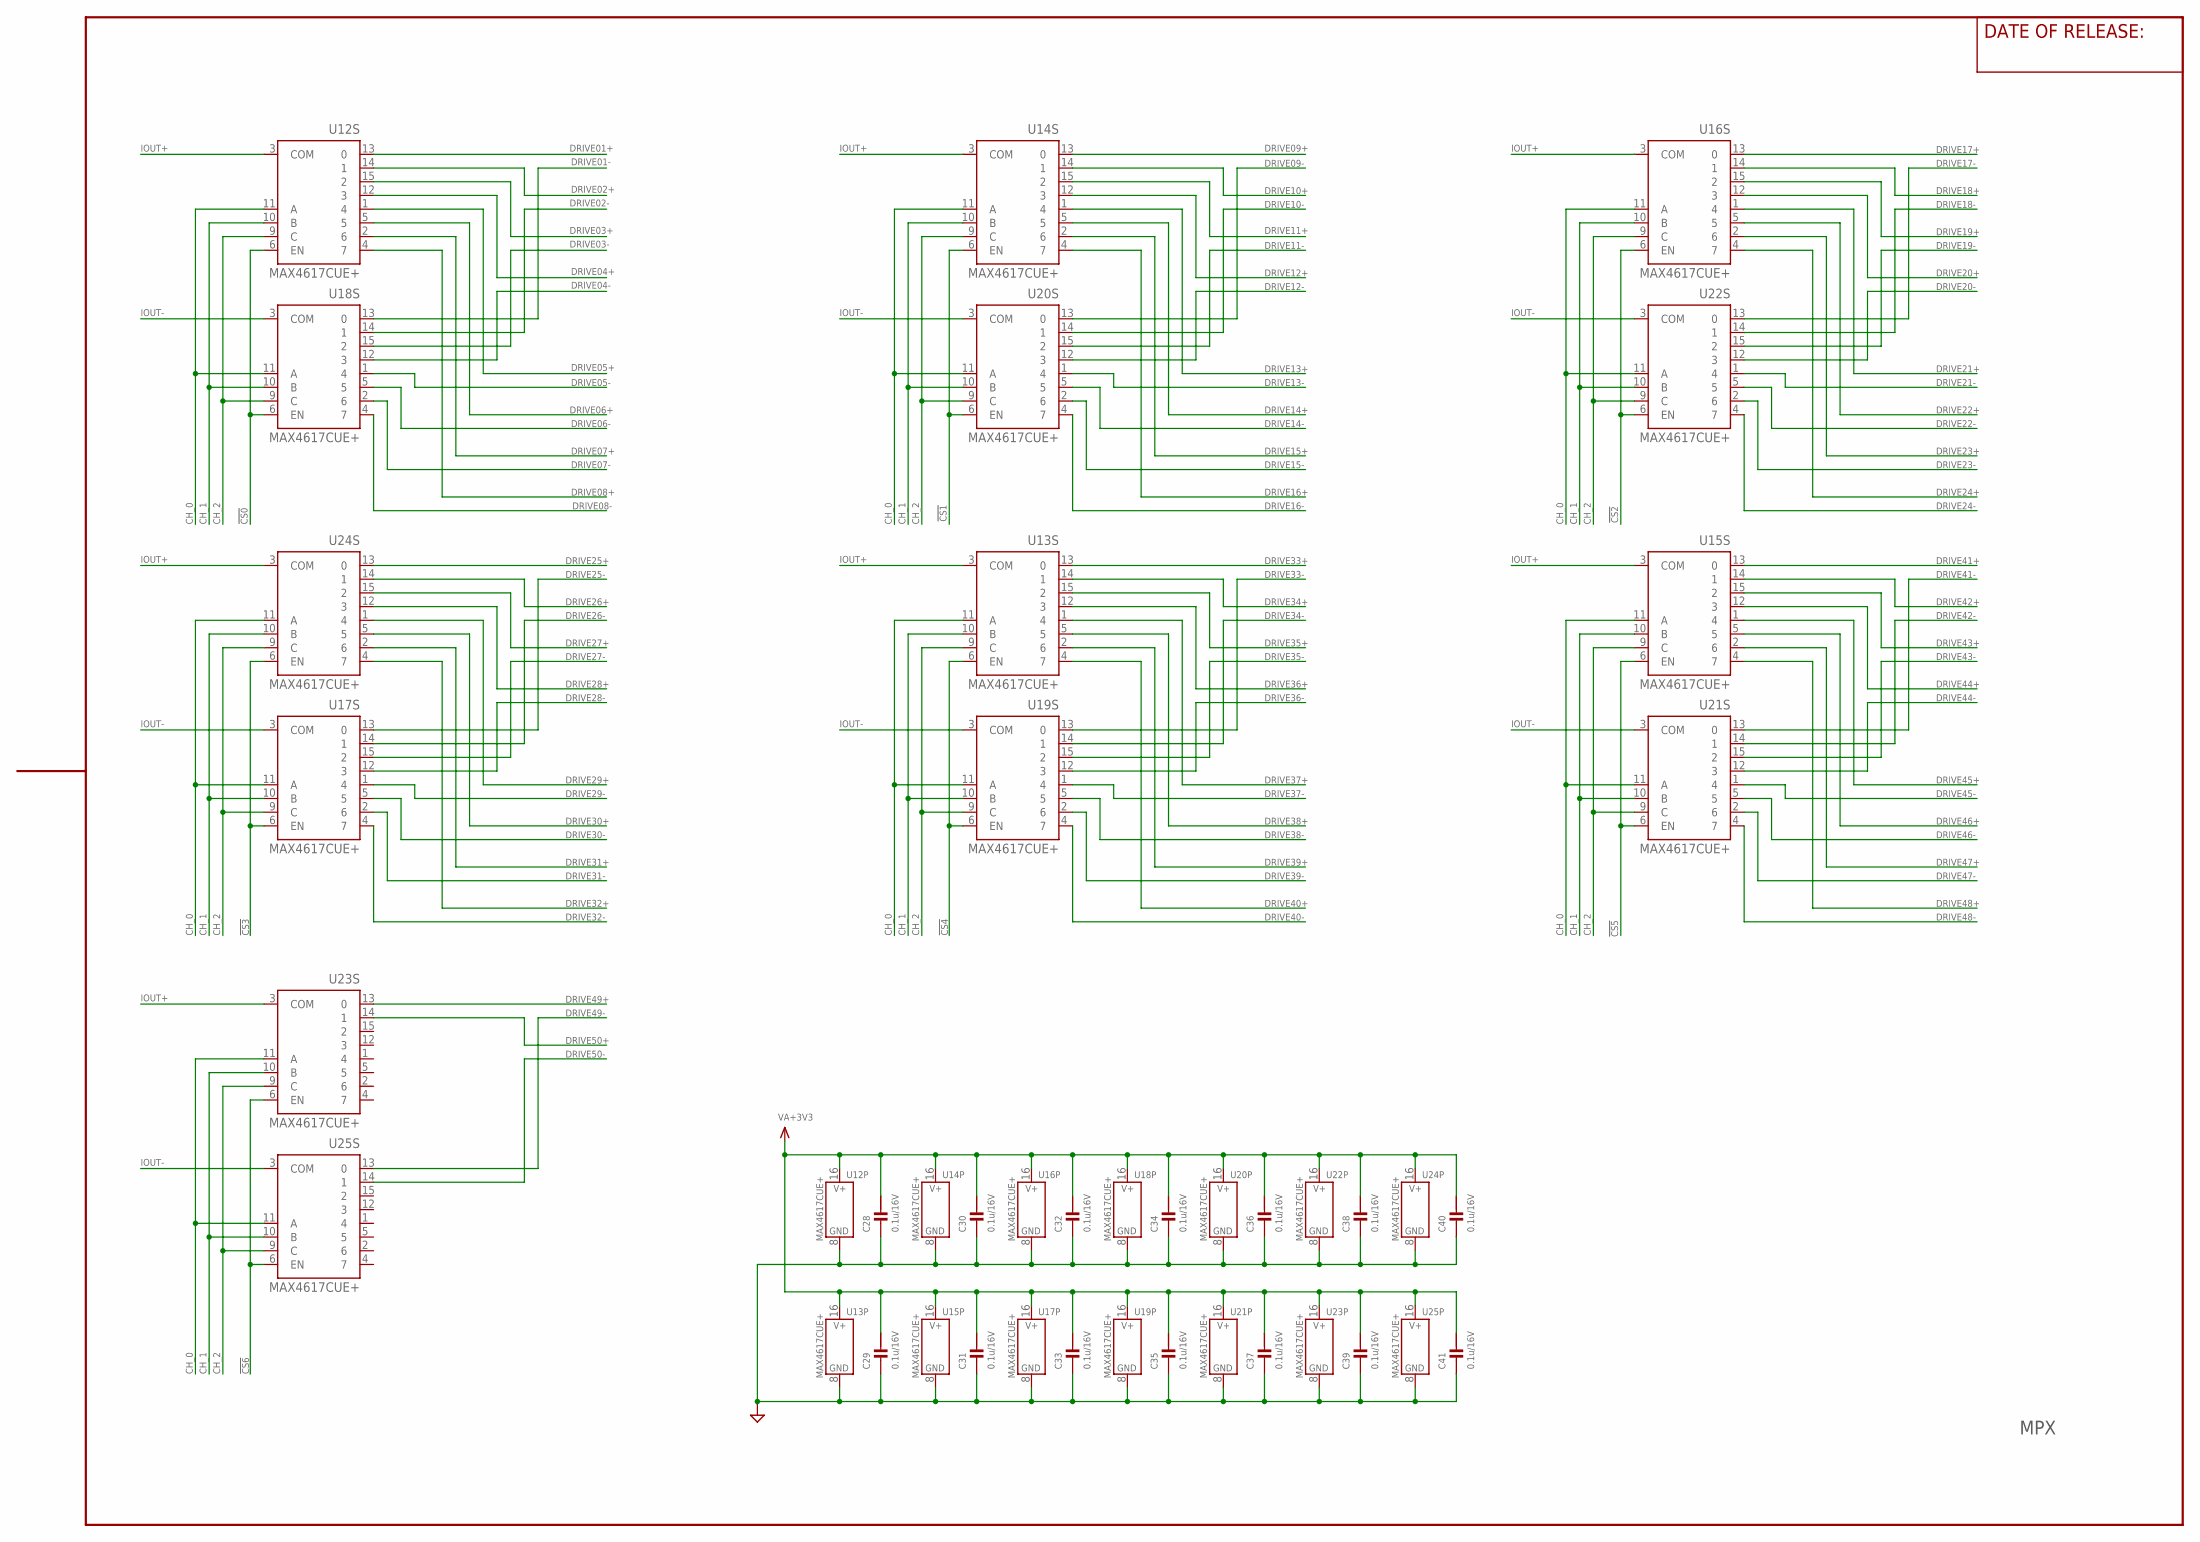
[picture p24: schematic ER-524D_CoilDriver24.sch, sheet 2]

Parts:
C28, C29, C30, C31, C32, C33, C34, C35, C36, C37, C38, C39, C40, C41: 0.1u/16V; CM1005
U12, U13, U14, U15, U16, U17, U18, U19, U20, U21, U22, U23, U24, U25: MAX4617CUE+; TSSOP16_AEL

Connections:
!CS0: U12.6 (EN), U18.6 (EN); also elsewhere on the board
!CS1: U14.6 (EN), U20.6 (EN); also elsewhere on the board
!CS2: U16.6 (EN), U22.6 (EN); also elsewhere on the board
!CS3: U17.6 (EN), U24.6 (EN); also elsewhere on the board
!CS4: U13.6 (EN), U19.6 (EN); also elsewhere on the board
!CS5: U15.6 (EN), U21.6 (EN); also elsewhere on the board
!CS6: U23.6 (EN), U25.6 (EN); also elsewhere on the board
AGND: C28.2, C29.2, C30.2, C31.2, C32.2, C33.2, C34.2, C35.2, C36.2, C37.2, C38.2, C39.2, C40.2, C41.2, U12.8 (V-), U13.8 (V-), U14.8 (V-), U15.8 (V-), U16.8 (V-), U17.8 (V-), U18.8 (V-), U19.8 (V-), U20.8 (V-), U21.8 (V-), U22.8 (V-), U23.8 (V-), U24.8 (V-), U25.8 (V-); also elsewhere on the board
CH_0: U12.11 (A), U13.11 (A), U14.11 (A), U15.11 (A), U16.11 (A), U17.11 (A), U18.11 (A), U19.11 (A), U20.11 (A), U21.11 (A), U22.11 (A), U23.11 (A), U24.11 (A), U25.11 (A); also elsewhere on the board
CH_1: U12.10 (B), U13.10 (B), U14.10 (B), U15.10 (B), U16.10 (B), U17.10 (B), U18.10 (B), U19.10 (B), U20.10 (B), U21.10 (B), U22.10 (B), U23.10 (B), U24.10 (B), U25.10 (B); also elsewhere on the board
CH_2: U12.9 (C), U13.9 (C), U14.9 (C), U15.9 (C), U16.9 (C), U17.9 (C), U18.9 (C), U19.9 (C), U20.9 (C), U21.9 (C), U22.9 (C), U23.9 (C), U24.9 (C), U25.9 (C); also elsewhere on the board
DRIVE01+: U12.13 (0); also elsewhere on the board
DRIVE01-: U18.13 (0); also elsewhere on the board
DRIVE02+: U12.14 (1); also elsewhere on the board
DRIVE02-: U18.14 (1); also elsewhere on the board
DRIVE03+: U12.15 (2); also elsewhere on the board
DRIVE03-: U18.15 (2); also elsewhere on the board
DRIVE04+: U12.12 (3); also elsewhere on the board
DRIVE04-: U18.12 (3); also elsewhere on the board
DRIVE05+: U12.1 (4); also elsewhere on the board
DRIVE05-: U18.1 (4); also elsewhere on the board
DRIVE06+: U12.5; also elsewhere on the board
DRIVE06-: U18.5; also elsewhere on the board
DRIVE07+: U12.2 (6); also elsewhere on the board
DRIVE07-: U18.2 (6); also elsewhere on the board
DRIVE08+: U12.4 (7); also elsewhere on the board
DRIVE08-: U18.4 (7); also elsewhere on the board
DRIVE09+: U14.13 (0); also elsewhere on the board
DRIVE09-: U20.13 (0); also elsewhere on the board
DRIVE10+: U14.14 (1); also elsewhere on the board
DRIVE10-: U20.14 (1); also elsewhere on the board
DRIVE11+: U14.15 (2); also elsewhere on the board
DRIVE11-: U20.15 (2); also elsewhere on the board
DRIVE12+: U14.12 (3); also elsewhere on the board
DRIVE12-: U20.12 (3); also elsewhere on the board
DRIVE13+: U14.1 (4); also elsewhere on the board
DRIVE13-: U20.1 (4); also elsewhere on the board
DRIVE14+: U14.5; also elsewhere on the board
DRIVE14-: U20.5; also elsewhere on the board
DRIVE15+: U14.2 (6); also elsewhere on the board
DRIVE15-: U20.2 (6); also elsewhere on the board
DRIVE16+: U14.4 (7); also elsewhere on the board
DRIVE16-: U20.4 (7); also elsewhere on the board
DRIVE17+: U16.13 (0); also elsewhere on the board
DRIVE17-: U22.13 (0); also elsewhere on the board
DRIVE18+: U16.14 (1); also elsewhere on the board
DRIVE18-: U22.14 (1); also elsewhere on the board
DRIVE19+: U16.15 (2); also elsewhere on the board
DRIVE19-: U22.15 (2); also elsewhere on the board
DRIVE20+: U16.12 (3); also elsewhere on the board
DRIVE20-: U22.12 (3); also elsewhere on the board
DRIVE21+: U16.1 (4); also elsewhere on the board
DRIVE21-: U22.1 (4); also elsewhere on the board
DRIVE22+: U16.5; also elsewhere on the board
DRIVE22-: U22.5; also elsewhere on the board
DRIVE23+: U16.2 (6); also elsewhere on the board
DRIVE23-: U22.2 (6); also elsewhere on the board
DRIVE24+: U16.4 (7); also elsewhere on the board
DRIVE24-: U22.4 (7); also elsewhere on the board
DRIVE25+: U24.13 (0); also elsewhere on the board
DRIVE25-: U17.13 (0); also elsewhere on the board
DRIVE26+: U24.14 (1); also elsewhere on the board
DRIVE26-: U17.14 (1); also elsewhere on the board
DRIVE27+: U24.15 (2); also elsewhere on the board
DRIVE27-: U17.15 (2); also elsewhere on the board
DRIVE28+: U24.12 (3); also elsewhere on the board
DRIVE28-: U17.12 (3); also elsewhere on the board
DRIVE29+: U24.1 (4); also elsewhere on the board
DRIVE29-: U17.1 (4); also elsewhere on the board
DRIVE30+: U24.5; also elsewhere on the board
DRIVE30-: U17.5; also elsewhere on the board
DRIVE31+: U24.2 (6); also elsewhere on the board
DRIVE31-: U17.2 (6); also elsewhere on the board
DRIVE32+: U24.4 (7); also elsewhere on the board
DRIVE32-: U17.4 (7); also elsewhere on the board
DRIVE33+: U13.13 (0); also elsewhere on the board
DRIVE33-: U19.13 (0); also elsewhere on the board
DRIVE34+: U13.14 (1); also elsewhere on the board
DRIVE34-: U19.14 (1); also elsewhere on the board
DRIVE35+: U13.15 (2); also elsewhere on the board
DRIVE35-: U19.15 (2); also elsewhere on the board
DRIVE36+: U13.12 (3); also elsewhere on the board
DRIVE36-: U19.12 (3); also elsewhere on the board
DRIVE37+: U13.1 (4); also elsewhere on the board
DRIVE37-: U19.1 (4); also elsewhere on the board
DRIVE38+: U13.5; also elsewhere on the board
DRIVE38-: U19.5; also elsewhere on the board
DRIVE39+: U13.2 (6); also elsewhere on the board
DRIVE39-: U19.2 (6); also elsewhere on the board
DRIVE40+: U13.4 (7); also elsewhere on the board
DRIVE40-: U19.4 (7); also elsewhere on the board
DRIVE41+: U15.13 (0); also elsewhere on the board
DRIVE41-: U21.13 (0); also elsewhere on the board
DRIVE42+: U15.14 (1); also elsewhere on the board
DRIVE42-: U21.14 (1); also elsewhere on the board
DRIVE43+: U15.15 (2); also elsewhere on the board
DRIVE43-: U21.15 (2); also elsewhere on the board
DRIVE44+: U15.12 (3); also elsewhere on the board
DRIVE44-: U21.12 (3); also elsewhere on the board
DRIVE45+: U15.1 (4); also elsewhere on the board
DRIVE45-: U21.1 (4); also elsewhere on the board
DRIVE46+: U15.5; also elsewhere on the board
DRIVE46-: U21.5; also elsewhere on the board
DRIVE47+: U15.2 (6); also elsewhere on the board
DRIVE47-: U21.2 (6); also elsewhere on the board
DRIVE48+: U15.4 (7); also elsewhere on the board
DRIVE48-: U21.4 (7); also elsewhere on the board
DRIVE49+: U23.13 (0); also elsewhere on the board
DRIVE49-: U25.13 (0); also elsewhere on the board
DRIVE50+: U23.14 (1); also elsewhere on the board
DRIVE50-: U25.14 (1); also elsewhere on the board
IOUT+: U12.3 (COM), U13.3 (COM), U14.3 (COM), U15.3 (COM), U16.3 (COM), U23.3 (COM), U24.3 (COM); also elsewhere on the board
IOUT-: U17.3 (COM), U18.3 (COM), U19.3 (COM), U20.3 (COM), U21.3 (COM), U22.3 (COM), U25.3 (COM); also elsewhere on the board
VA+3V3: C28.1, C29.1, C30.1, C31.1, C32.1, C33.1, C34.1, C35.1, C36.1, C37.1, C38.1, C39.1, C40.1, C41.1, U12.16 (V+), U13.16 (V+), U14.16 (V+), U15.16 (V+), U16.16 (V+), U17.16 (V+), U18.16 (V+), U19.16 (V+), U20.16 (V+), U21.16 (V+), U22.16 (V+), U23.16 (V+), U24.16 (V+), U25.16 (V+); also elsewhere on the board

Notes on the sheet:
MPX

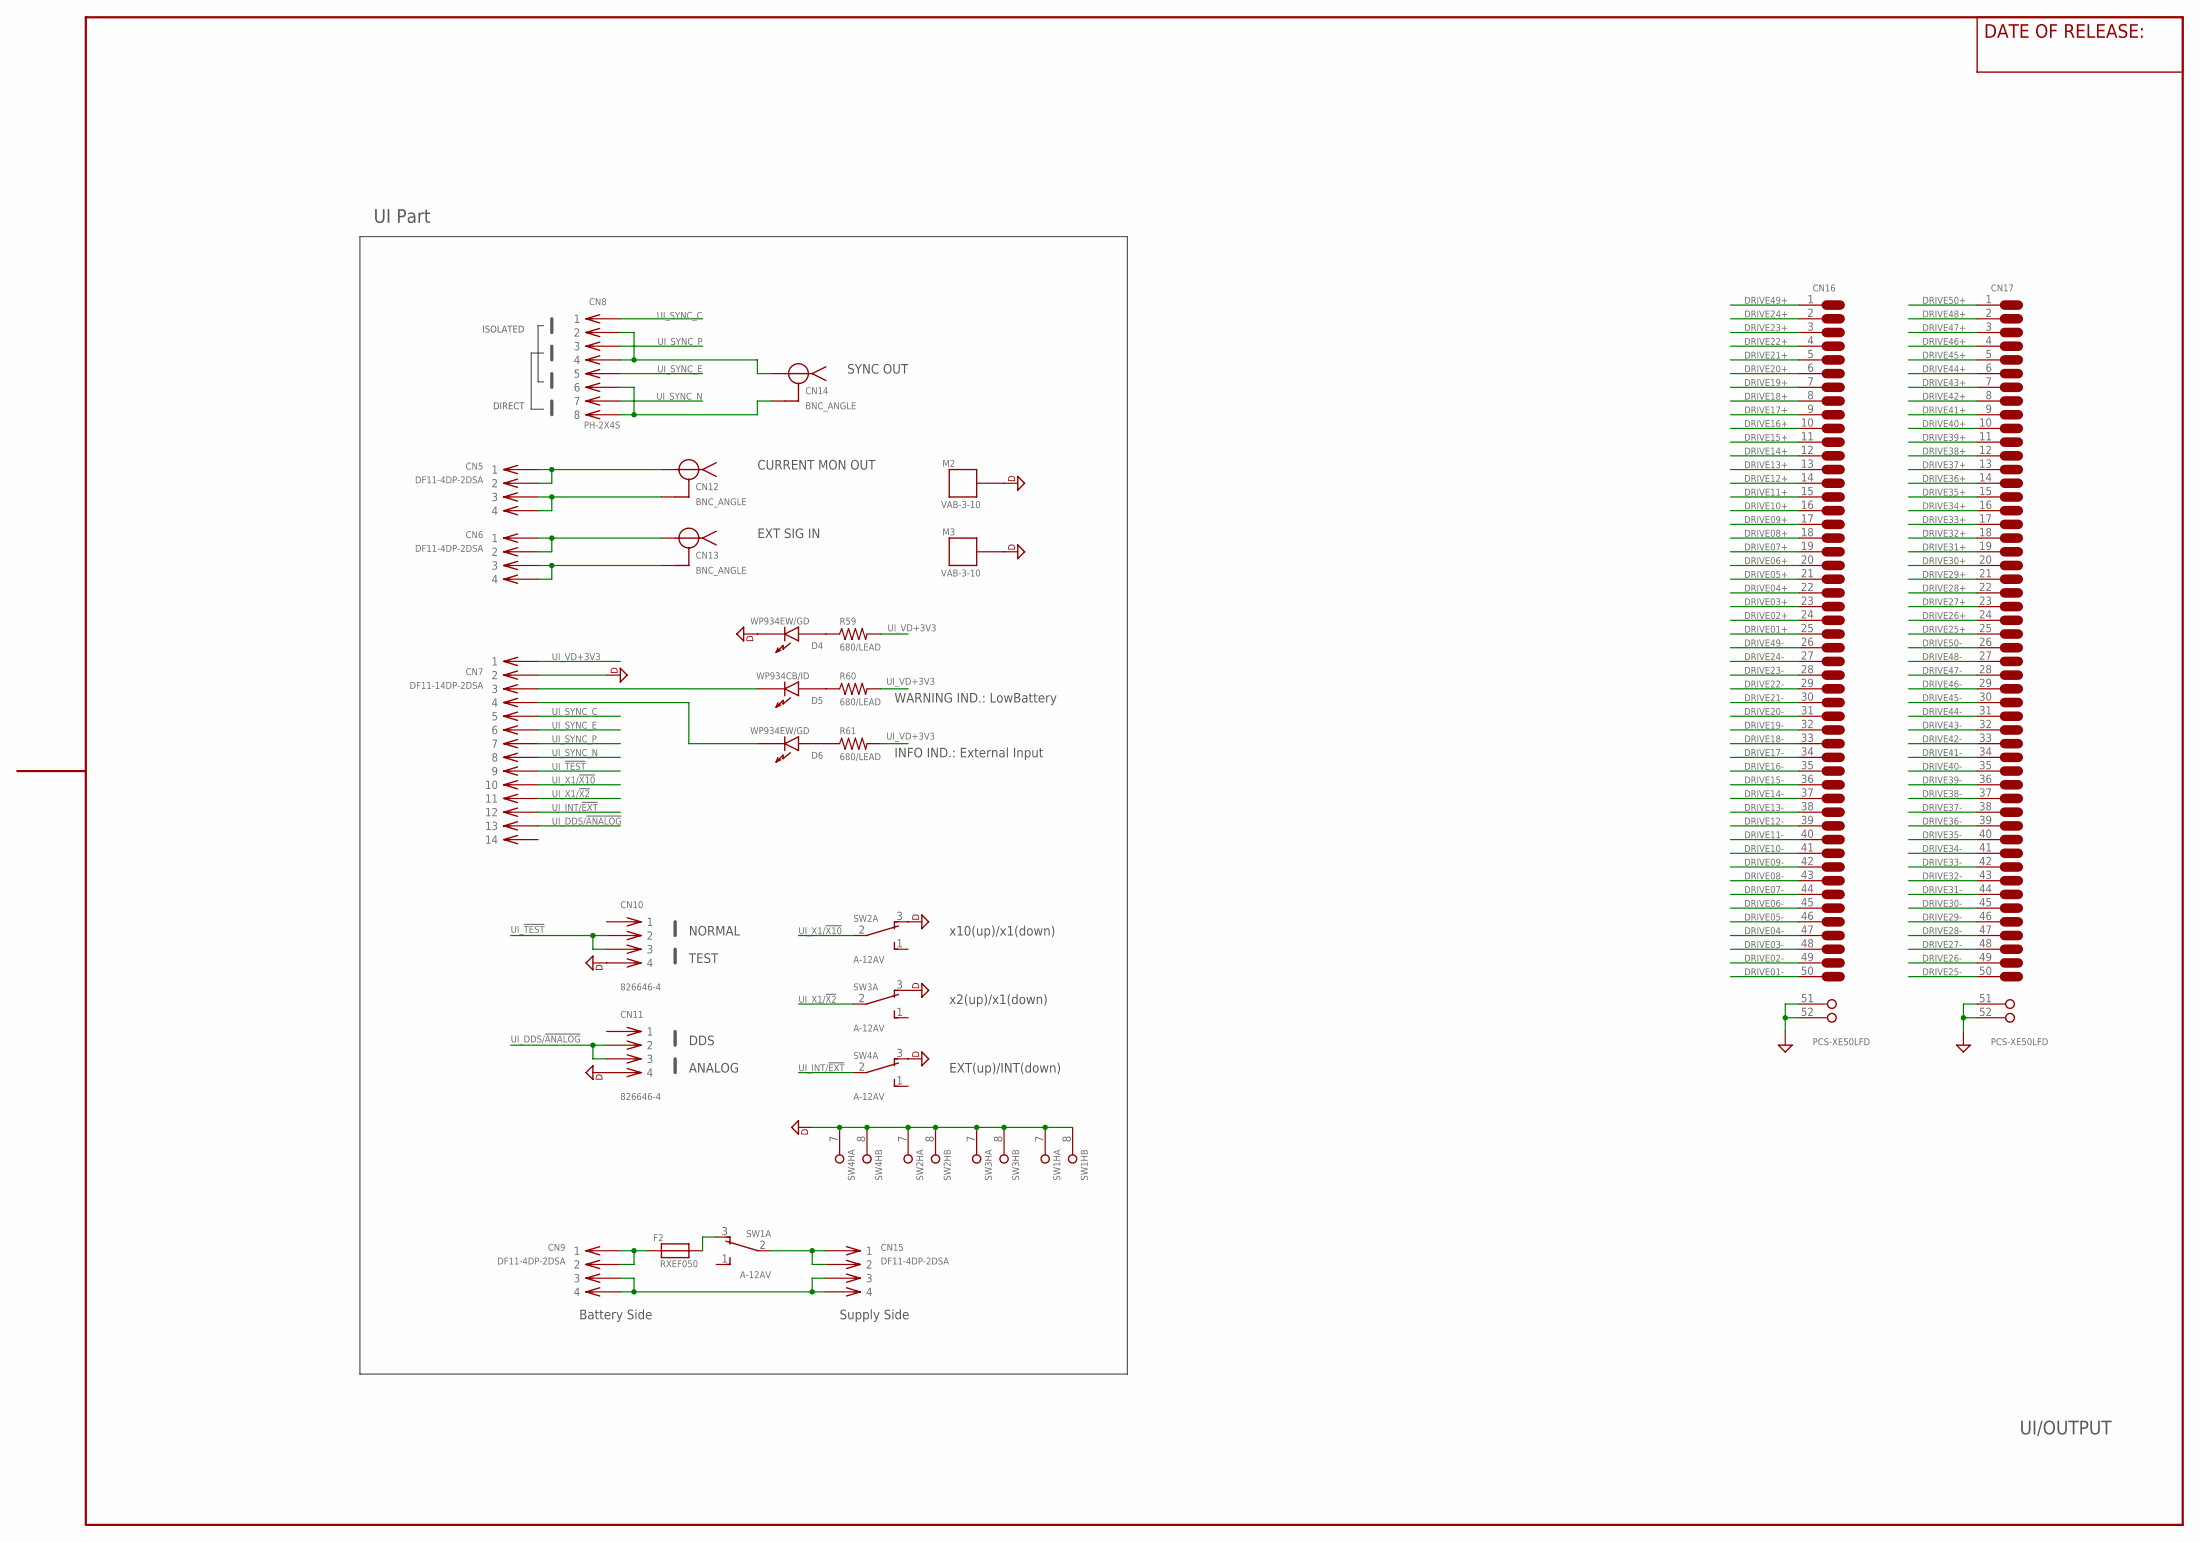
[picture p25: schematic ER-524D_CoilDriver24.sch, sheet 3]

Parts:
CN5, CN6, CN9, CN15: DF11-4DP-2DSA
CN7: DF11-14DP-2DSA
CN8: PH-2X4S; PIN_HEADER_8PIN
CN10, CN11: 826646-4; PIN_HEADER_4PIN
CN12, CN13, CN14: BNC_ANGLE; BNC_F_ANGLE
CN16, CN17: PCS-XE50LFD; 50LFD2
D4, D6: WP934EW/GD; L-93A8CB
D5: WP934CB/ID; L-93A8CB
F2: RXEF050; 8X3/5.08
M2, M3: VAB-3-10; VAB_3_10_CONTACT
R59, R60, R61: 680/LEAD; 0207/2V
SW1, SW2, SW3, SW4: A-12AV; A-12*

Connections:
AGND: CN16.51 (G1), CN16.52 (G2), CN17.51 (G1), CN17.52 (G2); also elsewhere on the board
DGND: CN7.2, CN10.4, CN11.4, D4.C (K1), M2.CASE1, M3.CASE1, SW1.7 (BRACKET), SW1.8 (BRACKET), SW2.3 (NC), SW2.7 (BRACKET), SW2.8 (BRACKET), SW3.3 (NC), SW3.7 (BRACKET), SW3.8 (BRACKET), SW4.3 (NC), SW4.7 (BRACKET), SW4.8 (BRACKET); also elsewhere on the board
DRIVE01+: CN16.25; also elsewhere on the board
DRIVE01-: CN16.50; also elsewhere on the board
DRIVE02+: CN16.24; also elsewhere on the board
DRIVE02-: CN16.49; also elsewhere on the board
DRIVE03+: CN16.23; also elsewhere on the board
DRIVE03-: CN16.48; also elsewhere on the board
DRIVE04+: CN16.22; also elsewhere on the board
DRIVE04-: CN16.47; also elsewhere on the board
DRIVE05+: CN16.21; also elsewhere on the board
DRIVE05-: CN16.46; also elsewhere on the board
DRIVE06+: CN16.20; also elsewhere on the board
DRIVE06-: CN16.45; also elsewhere on the board
DRIVE07+: CN16.19; also elsewhere on the board
DRIVE07-: CN16.44; also elsewhere on the board
DRIVE08+: CN16.18; also elsewhere on the board
DRIVE08-: CN16.43; also elsewhere on the board
DRIVE09+: CN16.17; also elsewhere on the board
DRIVE09-: CN16.42; also elsewhere on the board
DRIVE10+: CN16.16; also elsewhere on the board
DRIVE10-: CN16.41; also elsewhere on the board
DRIVE11+: CN16.15; also elsewhere on the board
DRIVE11-: CN16.40; also elsewhere on the board
DRIVE12+: CN16.14; also elsewhere on the board
DRIVE12-: CN16.39; also elsewhere on the board
DRIVE13+: CN16.13; also elsewhere on the board
DRIVE13-: CN16.38; also elsewhere on the board
DRIVE14+: CN16.12; also elsewhere on the board
DRIVE14-: CN16.37; also elsewhere on the board
DRIVE15+: CN16.11; also elsewhere on the board
DRIVE15-: CN16.36; also elsewhere on the board
DRIVE16+: CN16.10; also elsewhere on the board
DRIVE16-: CN16.35; also elsewhere on the board
DRIVE17+: CN16.9; also elsewhere on the board
DRIVE17-: CN16.34; also elsewhere on the board
DRIVE18+: CN16.8; also elsewhere on the board
DRIVE18-: CN16.33; also elsewhere on the board
DRIVE19+: CN16.7; also elsewhere on the board
DRIVE19-: CN16.32; also elsewhere on the board
DRIVE20+: CN16.6; also elsewhere on the board
DRIVE20-: CN16.31; also elsewhere on the board
DRIVE21+: CN16.5; also elsewhere on the board
DRIVE21-: CN16.30; also elsewhere on the board
DRIVE22+: CN16.4; also elsewhere on the board
DRIVE22-: CN16.29; also elsewhere on the board
DRIVE23+: CN16.3; also elsewhere on the board
DRIVE23-: CN16.28; also elsewhere on the board
DRIVE24+: CN16.2; also elsewhere on the board
DRIVE24-: CN16.27; also elsewhere on the board
DRIVE25+: CN17.25; also elsewhere on the board
DRIVE25-: CN17.50; also elsewhere on the board
DRIVE26+: CN17.24; also elsewhere on the board
DRIVE26-: CN17.49; also elsewhere on the board
DRIVE27+: CN17.23; also elsewhere on the board
DRIVE27-: CN17.48; also elsewhere on the board
DRIVE28+: CN17.22; also elsewhere on the board
DRIVE28-: CN17.47; also elsewhere on the board
DRIVE29+: CN17.21; also elsewhere on the board
DRIVE29-: CN17.46; also elsewhere on the board
DRIVE30+: CN17.20; also elsewhere on the board
DRIVE30-: CN17.45; also elsewhere on the board
DRIVE31+: CN17.19; also elsewhere on the board
DRIVE31-: CN17.44; also elsewhere on the board
DRIVE32+: CN17.18; also elsewhere on the board
DRIVE32-: CN17.43; also elsewhere on the board
DRIVE33+: CN17.17; also elsewhere on the board
DRIVE33-: CN17.42; also elsewhere on the board
DRIVE34+: CN17.16; also elsewhere on the board
DRIVE34-: CN17.41; also elsewhere on the board
DRIVE35+: CN17.15; also elsewhere on the board
DRIVE35-: CN17.40; also elsewhere on the board
DRIVE36+: CN17.14; also elsewhere on the board
DRIVE36-: CN17.39; also elsewhere on the board
DRIVE37+: CN17.13; also elsewhere on the board
DRIVE37-: CN17.38; also elsewhere on the board
DRIVE38+: CN17.12; also elsewhere on the board
DRIVE38-: CN17.37; also elsewhere on the board
DRIVE39+: CN17.11; also elsewhere on the board
DRIVE39-: CN17.36; also elsewhere on the board
DRIVE40+: CN17.10; also elsewhere on the board
DRIVE40-: CN17.35; also elsewhere on the board
DRIVE41+: CN17.9; also elsewhere on the board
DRIVE41-: CN17.34; also elsewhere on the board
DRIVE42+: CN17.8; also elsewhere on the board
DRIVE42-: CN17.33; also elsewhere on the board
DRIVE43+: CN17.7; also elsewhere on the board
DRIVE43-: CN17.32; also elsewhere on the board
DRIVE44+: CN17.6; also elsewhere on the board
DRIVE44-: CN17.31; also elsewhere on the board
DRIVE45+: CN17.5; also elsewhere on the board
DRIVE45-: CN17.30; also elsewhere on the board
DRIVE46+: CN17.4; also elsewhere on the board
DRIVE46-: CN17.29; also elsewhere on the board
DRIVE47+: CN17.3; also elsewhere on the board
DRIVE47-: CN17.28; also elsewhere on the board
DRIVE48+: CN17.2; also elsewhere on the board
DRIVE48-: CN17.27; also elsewhere on the board
DRIVE49+: CN16.1; also elsewhere on the board
DRIVE49-: CN16.26; also elsewhere on the board
DRIVE50+: CN17.1; also elsewhere on the board
DRIVE50-: CN17.26; also elsewhere on the board
unnamed: CN7.3, D5.C (K1)
unnamed: D5.A (A1), R60.1
unnamed: D6.A (A1), R61.1
unnamed: CN7.4, D6.C (K1)
unnamed: CN8.2, CN8.4, CN14.P$1
unnamed: CN8.6, CN8.8, CN14.P$2
unnamed: CN6.1, CN6.2, CN13.P$1
unnamed: CN6.3, CN6.4, CN13.P$2
unnamed: CN5.3, CN5.4, CN12.P$2
unnamed: CN5.1, CN5.2, CN12.P$1
unnamed: CN9.1, CN9.2, F2.1
unnamed: F2.2, SW1.3 (NC)
unnamed: CN9.3, CN9.4, CN15.3, CN15.4
unnamed: D4.A (A1), R59.1
unnamed: CN15.1, CN15.2, SW1.2 (C)
UI_!TEST!: CN7.9, CN10.2, CN10.3
UI_DDS/!ANALOG!: CN7.13, CN11.2, CN11.3
UI_INT/!EXT!: CN7.12, SW4.2 (C)
UI_SYNC_C: CN7.5, CN8.1
UI_SYNC_E: CN7.6, CN8.5
UI_SYNC_N: CN7.8, CN8.7
UI_SYNC_P: CN7.7, CN8.3
UI_VD+3V3: CN7.1, R59.2, R60.2, R61.2
UI_X1/!X2!: CN7.11, SW3.2 (C)
UI_X1/!X10!: CN7.10, SW2.2 (C)

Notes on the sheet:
UI/OUTPUT
WARNING IND.: LowBattery
INFO IND.: External Input
EXT(up)/INT(down)
x2(up)/x1(down)
x10(up)/x1(down)
NORMAL
TEST
DDS
ANALOG
SYNC OUT
ISOLATED
DIRECT
CURRENT MON OUT
EXT SIG IN
Battery Side
Supply Side
UI Part

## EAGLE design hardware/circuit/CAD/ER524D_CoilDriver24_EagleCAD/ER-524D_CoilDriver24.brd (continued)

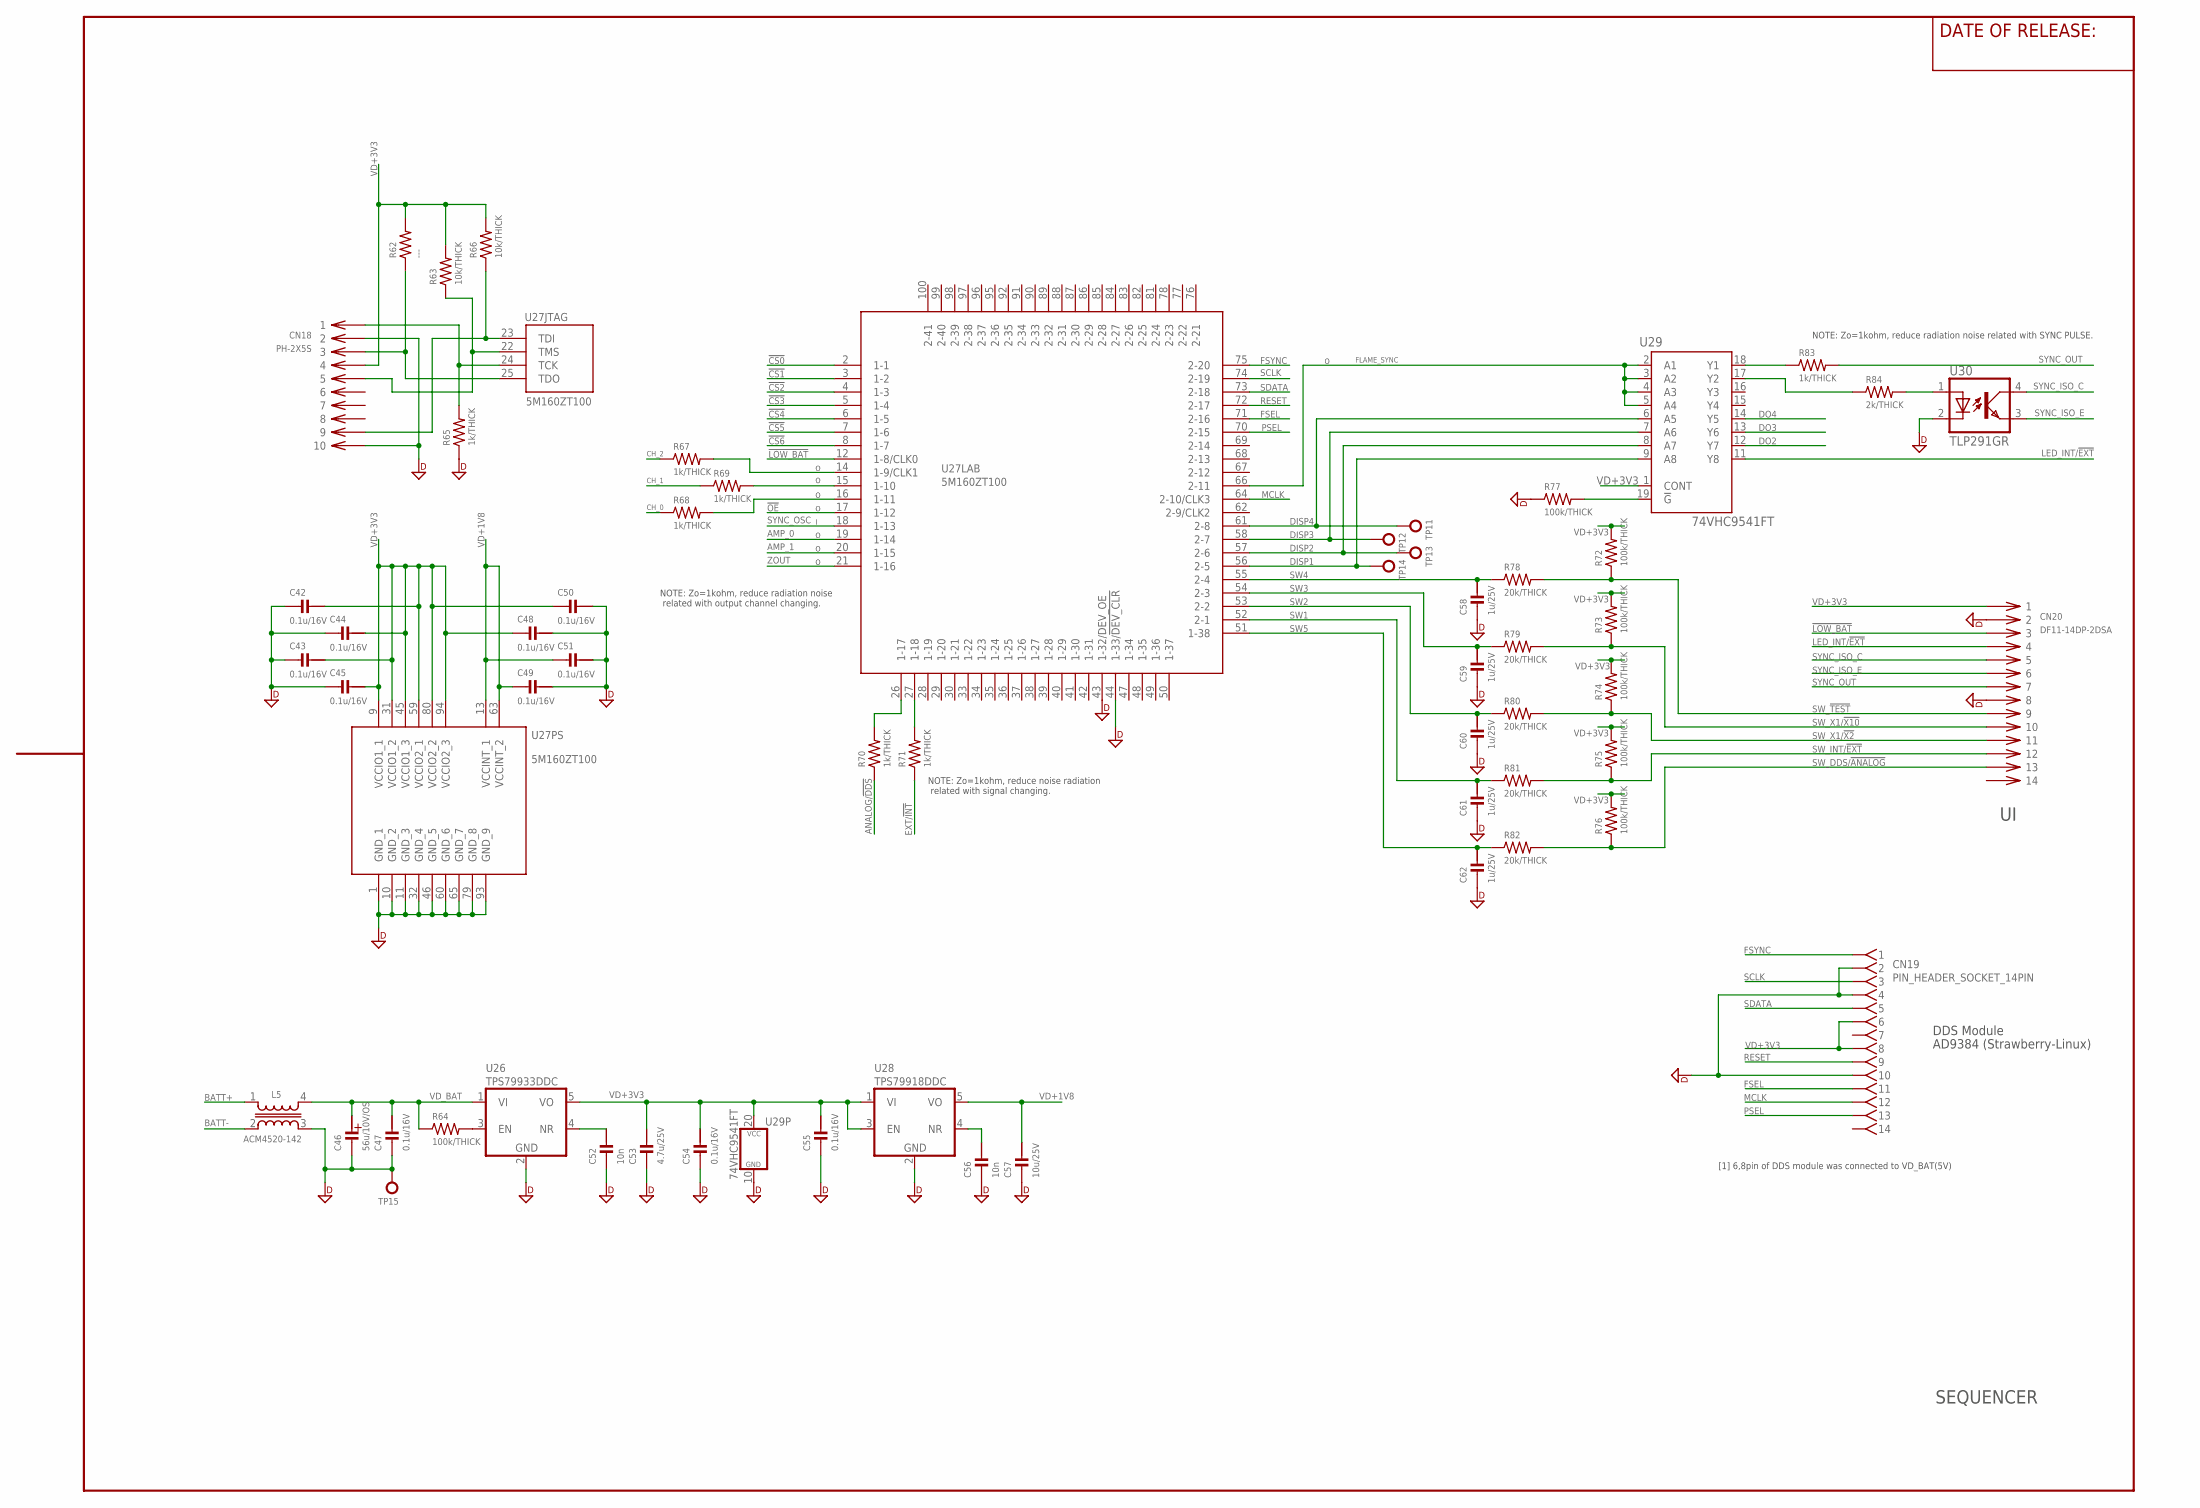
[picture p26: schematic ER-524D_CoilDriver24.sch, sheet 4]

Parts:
C42, C43, C44, C45, C47, C48, C49, C50, C51, C54, C55: 0.1u/16V; CM1005
C46: 56u/10V/OS; PHI_6.3
C52, C56: 10n; CM2012
C53: 4.7u/25V; CM2012
C57: 10u/25V; CM2012
C58, C59, C60, C61, C62: 1u/25V; CM1608
CN18: PH-2X5S; PIN_HEADER_10PIN
CN19: PIN_HEADER_SOCKET_14PIN
CN20: DF11-14DP-2DSA
L5: ACM4520-142; ACM4520
R62: ---; RM1608
R63, R66: 10k/THICK; RM1608
R64, R72, R73, R74, R75, R76, R77: 100k/THICK; RM1608
R65, R67, R68, R69, R70, R71, R83: 1k/THICK; RM1608
R78, R79, R80, R81, R82: 20k/THICK; RM1608
R84: 2k/THICK; RM1608
TP11, TP12, TP13, TP14: TP-1MM_PAD; TP_PAD_1MM
TP15: TP-LC3G; TP_TH_0R9MM
U26: TPS79933DDC; SOT-23-5
U27: 5M160ZT100; QFP100_0.5
U28: TPS79918DDC; SOT-23-5
U29: 74VHC9541FT; TSSOP20-P-0044-065A
U30: TLP291GR; SO4(11-3C1)(TOSHIBA)

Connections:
!CS0: U27.2 (1-1); also elsewhere on the board
!CS1: U27.3 (1-2); also elsewhere on the board
!CS2: U27.4 (1-3); also elsewhere on the board
!CS3: U27.5 (1-4); also elsewhere on the board
!CS4: U27.6 (1-5); also elsewhere on the board
!CS5: U27.7 (1-6); also elsewhere on the board
!CS6: U27.8 (1-7); also elsewhere on the board
!LOW_BAT: CN20.3, U27.12 (1-8/CLK0); also elsewhere on the board
!OE: U27.17 (1-12)
AMP_0: U27.19 (1-14); also elsewhere on the board
AMP_1: U27.20 (1-15); also elsewhere on the board
ANALOG/!DDS!: R70.1; also elsewhere on the board
BATT+: L5.1; also elsewhere on the board
BATT-: L5.2 (3); also elsewhere on the board
CH_0: R68.1; also elsewhere on the board
CH_1: R69.1; also elsewhere on the board
CH_2: R67.1; also elsewhere on the board
DGND: C42.2, C43.2, C44.2, C45.2, C46.NEG, C47.2, C48.1, C49.1, C50.1, C51.1, C52.2, C53.2, C54.2, C55.2, C56.2, C57.2, C58.2, C59.2, C60.2, C61.2, C62.2, CN18.2, CN18.10, CN19.2, CN19.4, CN19.10, CN20.2, CN20.8, L5.3 (4), R65.1, R77.1, TP15.1, U26.2 (GND), U27.1 (GND_1), U27.10 (GND_2), U27.11 (GND_3), U27.32 (GND_4), U27.43 (1-32/DEV_OE), U27.44 (1-33/!DEV_CLR), U27.46 (GND_5), U27.60 (GND_6), U27.65 (GND_7), U27.79 (GND_8), U27.93 (GND_9), U28.2 (GND), U29.10 (GND), U30.2 (C); also elsewhere on the board
DISP1: TP14.P$1, U27.56 (2-5), U29.9 (A8)
DISP2: TP13.P$1, U27.57 (2-6), U29.8 (A7)
DISP3: TP12.P$1, U27.58 (2-7), U29.7 (A6)
DISP4: TP11.P$1, U27.61 (2-8), U29.6 (A5)
DO2: U29.12 (Y7)
DO3: U29.13 (Y6)
DO4: U29.14 (Y5)
EXT/!INT!: R71.1; also elsewhere on the board
FLAME_SYNC: U27.66 (2-11), U29.2 (A1), U29.3 (A2), U29.4 (A3), U29.5 (A4)
FSEL: CN19.11, U27.71 (2-16)
FSYNC: CN19.1, U27.75 (2-20)
LED_INT/!EXT!: CN20.4, U29.11 (Y8)
MCLK: CN19.12, U27.64 (2-10/CLK3)
unnamed: R69.2, U27.15 (1-10)
unnamed: R68.2, U27.16 (1-11)
unnamed: R83.1, U29.18 (Y1)
unnamed: R77.2, U29.19 (!G)
unnamed: C52.1, U26.4 (NR)
unnamed: R64.2, U26.3 (EN)
unnamed: R70.2, U27.26 (1-17)
unnamed: CN18.9, R66.1, U27.23 (TDI)
unnamed: CN18.1, R65.2, U27.24 (TCK)
unnamed: R67.2, U27.14 (1-9/CLK1)
unnamed: R71.2, U27.27 (1-18)
unnamed: CN18.3, R62.1, U27.25 (TDO)
unnamed: CN18.5, R63.1, U27.22 (TMS)
unnamed: R84.1, U29.17 (Y2)
unnamed: C56.1, U28.4 (NR)
unnamed: R84.2, U30.1 (A)
PSEL: CN19.13, U27.70 (2-15)
RESET: CN19.9, U27.72 (2-17)
SCLK: CN19.3, U27.74 (2-19)
SDATA: CN19.5, U27.73 (2-18)
SW1: C61.1, R81.1, U27.52 (2-1)
SW2: C60.1, R80.1, U27.53 (2-2)
SW3: C59.1, R79.1, U27.54 (2-3)
SW4: C58.1, R78.1, U27.55 (2-4)
SW5: C62.1, R82.1, U27.51 (1-38)
SW_!TEST!: CN20.9, R72.1, R78.2
SW_DDS/!ANALOG!: CN20.13, R76.1, R82.2
SW_INT/!EXT: CN20.12, R75.1, R81.2
SW_X1/!X2!: CN20.11, R74.1, R80.2
SW_X1/!X10!: CN20.10, R73.1, R79.2
SYNC_ISO_C: CN20.5, U30.4 (COL)
SYNC_ISO_E: CN20.6, U30.3 (EMI)
SYNC_OSC: U27.18 (1-13); also elsewhere on the board
SYNC_OUT: CN20.7, R83.2
VD+1V8: C49.2, C51.2, C57.1, U27.13 (VCCINT_1), U27.63 (VCCINT_2), U28.5 (VO)
VD+3V3: C42.1, C43.1, C44.1, C45.1, C48.2, C50.2, C53.1, C54.1, C55.1, CN18.4, CN19.6, CN19.8, CN20.1, R62.2, R63.2, R66.2, R72.2, R73.2, R74.2, R75.2, R76.2, U26.5 (VO), U27.9 (VCCIO1_1), U27.31 (VCCIO1_2), U27.45 (VCCIO1_3), U27.59 (VCCIO2_1), U27.80 (VCCIO2_2), U27.94 (VCCIO2_3), U28.1 (VI), U28.3 (EN), U29.1 (CONT), U29.20 (VCC); also elsewhere on the board
VD_BAT: C46.POS, C47.1, L5.4 (2), R64.1, U26.1 (VI); also elsewhere on the board
ZOUT: U27.21 (1-16); also elsewhere on the board

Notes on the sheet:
SEQUENCER
DDS Module
AD9384 (Strawberry-Linux)
[1] 6,8pin of DDS module was connected to VD_BAT(5V)
NOTE: Zo=1kohm, reduce radiation noise related with SYNC PULSE.
NOTE: Zo=1kohm, reduce radiation noise related with output channel changing.
NOTE: Zo=1kohm, reduce noise radiation related with signal changing.

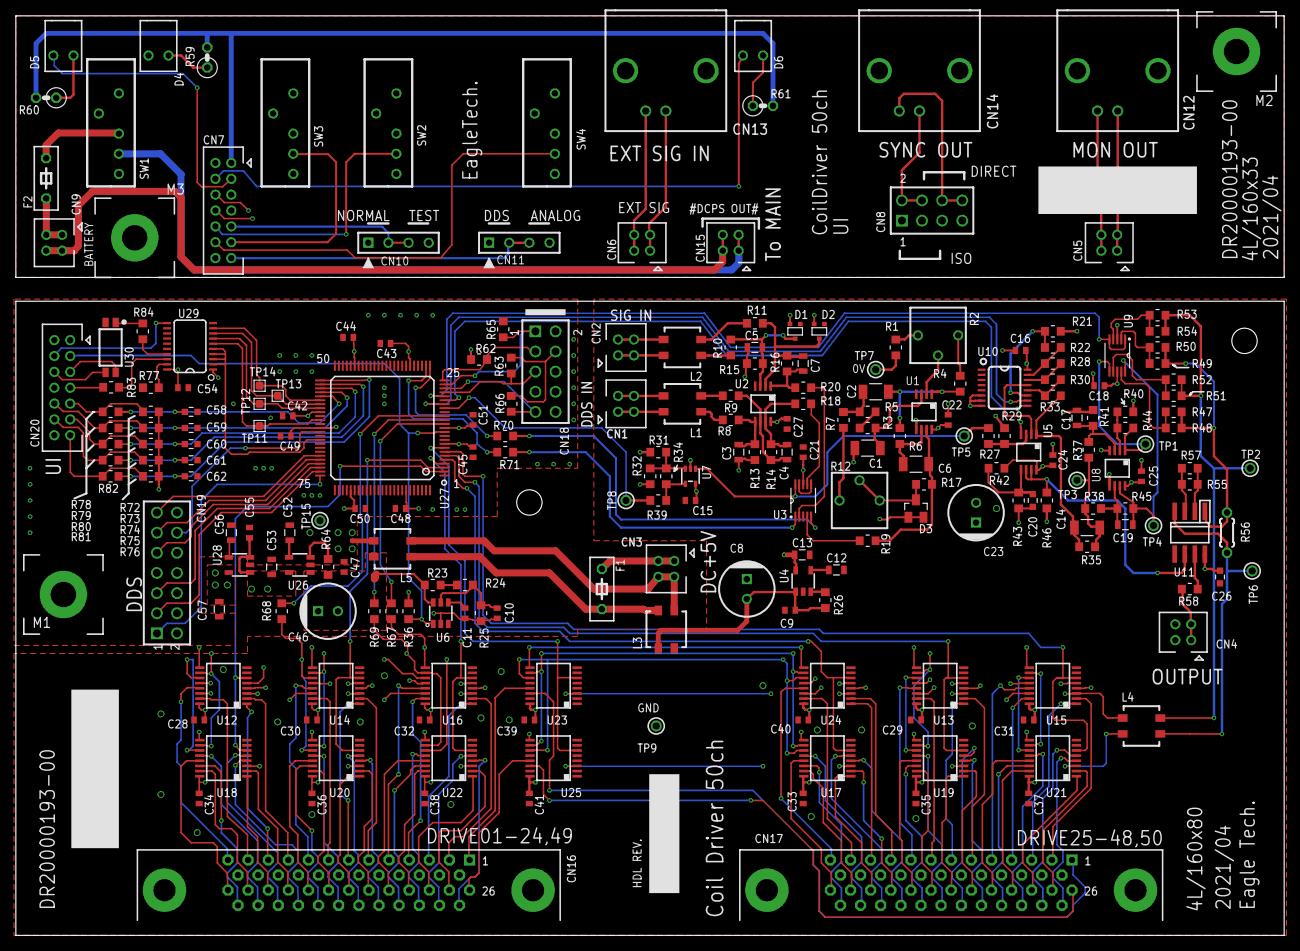
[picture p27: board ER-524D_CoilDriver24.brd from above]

Board: 4 copper layers, 160.0 x 116.0 mm, 231 parts (0 on the bottom side), 260 nets.

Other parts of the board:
U$2: 3MM_STAT

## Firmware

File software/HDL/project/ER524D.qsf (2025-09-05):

# -------------------------------------------------------------------------- #
#
# Copyright (C) 2019  Intel Corporation. All rights reserved.
# Your use of Intel Corporation's design tools, logic functions
# and other software and tools, and any partner logic
# functions, and any output files from any of the foregoing
# (including device programming or simulation files), and any
# associated documentation or information are expressly subject
# to the terms and conditions of the Intel Program License
# Subscription Agreement, the Intel Quartus Prime License Agreement,
# the Intel FPGA IP License Agreement, or other applicable license
# agreement, including, without limitation, that your use is for
# the sole purpose of programming logic devices manufactured by
# Intel and sold by Intel or its authorized distributors.  Please
# refer to the applicable agreement for further details, at
# https://fpgasoftware.intel.com/eula.
#
# -------------------------------------------------------------------------- #
#
# Quartus Prime
# Version 19.1.0 Build 670 09/22/2019 SJ Lite Edition
# Date created = 08:14:32  May 07, 2020
#
# -------------------------------------------------------------------------- #
#
# Notes:
#
# 1) The default values for assignments are stored in the file:
#		ER524D_assignment_defaults.qdf
#    If this file doesn't exist, see file:
#		assignment_defaults.qdf
#
# 2) Altera recommends that you do not modify this file. This
#    file is updated automatically by the Quartus Prime software
#    and any changes you make may be lost or overwritten.
#
# -------------------------------------------------------------------------- #


set_global_assignment -name FAMILY "MAX V"
set_global_assignment -name DEVICE 5M160ZT100I5
set_global_assignment -name TOP_LEVEL_ENTITY PhantomDriver
set_global_assignment -name ORIGINAL_QUARTUS_VERSION 23.1STD.1
set_global_assignment -name PROJECT_CREATION_TIME_DATE "15:24:31  SEPTEMBER 05, 2025"
set_global_assignment -name LAST_QUARTUS_VERSION "23.1std.1 Lite Edition"
set_global_assignment -name PROJECT_OUTPUT_DIRECTORY output_files
set_global_assignment -name MIN_CORE_JUNCTION_TEMP "-40"
set_global_assignment -name MAX_CORE_JUNCTION_TEMP 125
set_global_assignment -name DEVICE_FILTER_PACKAGE TQFP
set_global_assignment -name DEVICE_FILTER_PIN_COUNT 100
set_global_assignment -name DEVICE_FILTER_SPEED_GRADE 5
set_global_assignment -name ERROR_CHECK_FREQUENCY_DIVISOR "-1"
set_global_assignment -name EDA_SIMULATION_TOOL "Questa Intel FPGA (VHDL)"
set_global_assignment -name EDA_TIME_SCALE "1 ps" -section_id eda_simulation
set_global_assignment -name EDA_OUTPUT_DATA_FORMAT VHDL -section_id eda_simulation
set_global_assignment -name EDA_GENERATE_FUNCTIONAL_NETLIST OFF -section_id eda_board_design_timing
set_global_assignment -name EDA_GENERATE_FUNCTIONAL_NETLIST OFF -section_id eda_board_design_symbol
set_global_assignment -name EDA_GENERATE_FUNCTIONAL_NETLIST OFF -section_id eda_board_design_signal_integrity
set_global_assignment -name EDA_GENERATE_FUNCTIONAL_NETLIST OFF -section_id eda_board_design_boundary_scan
set_global_assignment -name POWER_PRESET_COOLING_SOLUTION "NO HEAT SINK WITH STILL AIR"
set_location_assignment PIN_20 -to AMP[1]
set_location_assignment PIN_19 -to AMP[0]
set_location_assignment PIN_14 -to CH[2]
set_location_assignment PIN_15 -to CH[1]
set_location_assignment PIN_16 -to CH[0]
set_location_assignment PIN_18 -to CLK
set_location_assignment PIN_8 -to CS[6]
set_location_assignment PIN_7 -to CS[5]
set_location_assignment PIN_6 -to CS[4]
set_location_assignment PIN_5 -to CS[3]
set_location_assignment PIN_4 -to CS[2]
set_location_assignment PIN_3 -to CS[1]
set_location_assignment PIN_2 -to CS[0]
set_location_assignment PIN_61 -to D[4]
set_location_assignment PIN_58 -to D[3]
set_location_assignment PIN_57 -to D[2]
set_location_assignment PIN_56 -to D[1]
set_location_assignment PIN_71 -to FSEL
set_location_assignment PIN_75 -to FSYNC
set_location_assignment PIN_64 -to MCLK
set_location_assignment PIN_70 -to PSEL
set_location_assignment PIN_72 -to RESET
set_location_assignment PIN_74 -to SCLK
set_location_assignment PIN_73 -to SDATA
set_location_assignment PIN_55 -to SW[4]
set_location_assignment PIN_54 -to SW[3]
set_location_assignment PIN_53 -to SW[2]
set_location_assignment PIN_52 -to SW[1]
set_location_assignment PIN_66 -to SYNC
set_location_assignment PIN_21 -to ZOUT
set_location_assignment PIN_17 -to OE
set_instance_assignment -name IO_STANDARD "3.3V SCHMITT TRIGGER INPUT" -to LOW_BAT
set_location_assignment PIN_12 -to LOW_BAT
set_location_assignment PIN_51 -to SW[5]
set_location_assignment PIN_26 -to SEL_ANALOG
set_location_assignment PIN_27 -to SEL_EXT
set_global_assignment -name VHDL_FILE SEQUENCER.vhdl
set_global_assignment -name VHDL_FILE PhantomDriver_tb.vhdl
set_global_assignment -name VHDL_FILE PhantomDriver.vhdl
set_global_assignment -name VHDL_FILE OUTPUT_PATCH.vhdl
set_global_assignment -name VHDL_FILE DDS_INIT.vhdl
set_global_assignment -name VHDL_FILE counter_increment.vhdl
set_global_assignment -name VHDL_FILE counter_decrement.vhdl
set_instance_assignment -name IO_STANDARD "3.3V SCHMITT TRIGGER INPUT" -to SW[5]
set_instance_assignment -name IO_STANDARD "3.3V SCHMITT TRIGGER INPUT" -to SW[4]
set_instance_assignment -name IO_STANDARD "3.3V SCHMITT TRIGGER INPUT" -to SW[3]
set_instance_assignment -name IO_STANDARD "3.3V SCHMITT TRIGGER INPUT" -to SW[2]
set_instance_assignment -name IO_STANDARD "3.3V SCHMITT TRIGGER INPUT" -to SW[1]
set_instance_assignment -name IO_STANDARD "3.3V SCHMITT TRIGGER INPUT" -to SW
set_instance_assignment -name IO_STANDARD "3.3-V LVTTL" -to SYNC
set_global_assignment -name MIF_FILE patch_table.mif

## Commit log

2025-05-29 README.md修正中
2025-06-10 update circuit/design_note
2025-07-11 update design_note and files
    [ER-524D_CoilDriver24.brd, ER-524D_CoilDriver24.sch, harness_set.sch]
2025-07-28 値づけ手順の追加
2025-08-06 値づけ手順 追記
2025-09-05 CalCoilDriver_Cal_block.drawio を追加しました。
2025-09-05 CalCoilDriver_Cal_block.drawio を更新します
2025-09-05 CalCoilDriver_Cal_block.png を追加しました。
2025-09-05 update /README & /calibration
2025-09-24 HDL_DDS_INIT.drawio を追加しました。
2025-09-24 HDL_DDS_INIT.drawio を更新します
2025-09-24 HDL_DDS_INIT.drawio.png を追加しました。
2025-09-25 ER524D_HDL_TopLevel_BlockDiagram.drawio を追加しました。
2025-09-25 ER524D_HDL_TopLevel_BlockDiagram.drawio を更新します
2025-09-25 ER524D_HDL_TopLevel_BlockDiagram.drawio.png を追加しました。
